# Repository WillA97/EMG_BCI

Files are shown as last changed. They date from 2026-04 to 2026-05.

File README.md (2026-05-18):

# EMG_BCI

## Introduction
This repository contains the documentation, hardware files, and software files for a simple electromyogram front end. The purpose is to create a simple interface to aquire the signals and also improve my hardware and software design skills. It's mostly for fun

## High level requirements

- Amplifier the signals from a 2 electrode from an EMG signal
- transfer the data from to a secondary device

## Hardware block diagram

```mermaid
graph TD
    A[EMG Electrodes<br>500 µV - 1 mV] --> B[Instrumentation Amplifier<br>Gain: 50<br>High Z, High CMRR]
    B --> C[High-Pass Filter<br>Cutoff: 10 Hz]
    C --> D[Gain Stage<br>Gain: 20<br>Total Gain: 1000]
    D --> E[Low-Pass Filter<br>Cutoff: 500 Hz]
    E --> F[Rectifier]
    E --> G[Offset Stage<br>Shift to 1.5V]
    G --> H[ADC 1<br>Un-rectified]
    F --> I[ADC 2<br>Rectified]

```
- The EMG signals will be around 500 uV - 1 mV. Will scale the signals with a gain of about 1000 to make the output swing around 0.5 - 1 V
- The first stage is the instrumentation amplifier. It has a very high impedence input, and large common mode rejection. It also has a gain stage built in, which is chosen as 50
- The second stage would be the high pass filter. Removed any high frequency signals and prevents aliasing when sampling occurs. The cutoff frequency is 10 Hz, which is the lower frequency of the muscle fibers
- The third stage is a gain stage. The gain is set to 20, putting the final gain at 1000.
- The fourth state is the low pass filter. The cutoff frequency was set to 500 Hz, which is the upper limit of the muscle fibers.
- The fifth stage is the rectifier stage.
- The sixth stage is the offset stage, which adds an offset to shift the 0 point of the signal to be 1.5V. This is because many microcontrollers use +3.3V and we want to avoid applying a negative voltage on the ADC
- The sevent stage is the ADC, which can record the EMG signals. To give some options about which signal can be used in the signal processing. I want to use one ADC for the un-rectified signal, and another for the rectified signal.

- There are a couple of options when using the signal for an EMG:
  
  - one option is to use the raw EMG data and do the signal processing on those values. After performing an FFT will get the frequency data from them
  - another option is to rectify the signal, this would give an positive average value for the signal
  - with the rectified signal, can take the RMS and filterd values of it to get the average value of the amount of exertion from the muscles
 
## Communication interface

- The communication interface will be used to transfer the digitized EMG signals to an external device. The ADC chosen (MCP 3202) uses an SPI interface.

## Test results 
Here are some of the results from testing the front end. The analog discovery module was used to insert a signal at the front of the instrumentation amplifier and the output at the different test points was recorded

### Instrumentation amplifier
The following table shows in the input and outputs for the instrumentation amplifier stage:

| Input | Offset | Output PK1 | Output PK2 | Out Offset | Diff | Gain | Offset Gain |
| :--- | :--- | :--- | :--- | :--- | :--- | :--- | :--- |
| 0.01 | 0.5 | 1.478 | 1.5204 | 1.4992 | 0.0424 | 4.24 | 1.8984 |
| 0.05 | 0.5 | 1.398 | 1.598 | 1.498 | 0.2 | 4 | 1.896 |
| 0.06 | 0.5 | 1.381 | 1.6175 | 1.49925 | 0.2365 | 3.94166667 | 1.8985 |
| 0.1 | 0.5 | 1.3 | 1.695 | 1.4975 | 0.395 | 3.95 | 1.895 |
| 0.15 | 0.5 | 1.202 | 1.796 | 1.499 | 0.594 | 3.96 | 1.898 |
| 0.05 | 0.1 | 0.621 | 0.819 | 0.72 | 0.198 | 3.96 | 1.7 |
| 0.05 | 0.2 | 0.814 | 1.01 | 0.912 | 0.196 | 3.92 | 1.81 |
| 0.05 | 0.4 | 1.207 | 1.402 | 1.3045 | 0.195 | 3.9 | 1.88625 |
| 0.05 | 0.6 | 1.596 | 1.792 | 1.694 | 0.196 | 3.92 | 1.90666667 |
| 0.05 | 0.7 | 1.789 | 1.985 | 1.887 | 0.196 | 3.92 | 1.91 |
| 0.05 | 0.8 | 1.984 | 2.181 | 2.0825 | 0.197 | 3.94 | 1.915625 |
| 0.05 | 0.9 | 2.181 | 2.376 | 2.2785 | 0.195 | 3.9 | 1.92055556 |
| 0.05 | 0 | 0.547 | 0.626 | 0.5865 | 0.079 | 1.58 | *Undefined (NaN)* |

couple of things to note:
- for some reason the gain of the amplifier is 4. From the datasheet since the gain pins is connected to HIGH it should be 50. Not sure why it isn't working as it should. Will have to do more investigation
- the offset did not work as I expected. It just cut off the zero point of the amplifier so when a negative value was put in, it was still cut off. I should have connected a negative supply to it in order to not lose the negative information or apply an offset to it using a summing amplifer. Since there is a high pass filter after it, the offset would likely removed anyways.

### TP2 - Output of the high pass filter and gain stage

The following table shows the data:

| Input | offset | output pk1 | output pk2 | out offset | diff | gain |
| :--- | :--- | :--- | :--- | :--- | :--- | :--- |
| 0.01 | 0.5 | -0.406 | 0.388 | -0.018 | 0.794 | 79.4 |
| 0.001 | 0.5 | -0.0375 | 0.0429 | 0.0054 | 0.0804 | 80.4 |
| 0.015 | 0.5 | -0.59 | 0.602 | 0.012 | 1.192 | 79.46667 |
| 0.02 | 0.5 | -0.782 | 0.798 | 0.016 | 1.58 | 79 |
| 0.03 | 0.5 | -1.118 | 1.1959 | 0.0159 | 2.3759 | 79.19667 |

### TP3 - Output of the low pass filter / The entire system

| Input | offset | output pk1 | output pk2 | out offset | diff | gain |
| :--- | :--- | :--- | :--- | :--- | :--- | :--- |
| 0.03 | 0.5 | -1.00E-02 | 5.64E-03 | -2.20E-03 | 1.57E-02 | 0.522333 |
| 0.03 | 0.5 | -6.79E-01 | 6.79E-01 | 0.00E+00 | 1.36E+00 | 45.26667 |
| 0.03 | 0.5 | -1.178 | 1.178 | 0.00E+00 | 2.36E+00 | 78.53333 |
| 0.03 | 0.5 | -1.178 | 1.178 | 0.00E+00 | 2.36E+00 | 78.53333 |
| 0.03 | 0.5 | -1.178 | 1.178 | 0.00E+00 | 2.36E+00 | 78.53333 |
| 0.03 | 0.5 | -1.1315 | 1.131 | -2.50E-04 | 2.26E+00 | 75.41667 |
| 0.03 | 0.5 | -1.014 | 1.014 | 0.00E+00 | 2.03E+00 | 67.6 |
| 0.03 | 0.5 | -8.62E-01 | 8.68E-01 | 3.00E-03 | 1.73E+00 | 57.66667 |
| 0.03 | 0.5 | -7.10E-01 | 7.04E-01 | -3.00E-03 | 1.41E+00 | 47.13333 |
| 0.03 | 0.5 | -5.64E-01 | 5.70E-01 | 3.00E-03 | 1.13E+00 | 37.8 |
| 0.03 | 0.5 | -4.70E-01 | 4.59E-01 | -5.50E-03 | 9.29E-01 | 30.96667 |
| 0.03 | 0.5 | -3.65E-01 | 3.71E-01 | 3.00E-03 | 7.36E-01 | 24.53333 |
| 0.03 | 0.5 | -3.12E-01 | 3.12E-01 | 0.00E+00 | 6.24E-01 | 20.8 |
| 0.03 | 0.5 | -2.01E-01 | 2.01E-01 | 0.00E+00 | 4.02E-01 | 13.4 |
| 0.03 | 0.5 | -1.45E-01 | 1.42E-01 | -1.50E-03 | 2.87E-01 | 9.566667 |
| 0.03 | 0

The graphs of the final table are:



The frequency response has the desired shape. The cutoff frequnecy is around 500 Hz. However, since the gain stage of the instrumentation amplifier was off for some reason, the final gain is off as well. This is annoying.

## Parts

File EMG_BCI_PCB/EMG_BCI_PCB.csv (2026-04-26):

Id | Designator | Footprint | Quantity | Designation | Supplier and ref
1 | U3,U2 | TSSOP-14_4.4x5mm_P0.65mm | 2 | ADA4807-4ARUZ
2 | C4,C25,C1,C3,C27 | C_0603_1608Metric_Pad1.08x0.95mm_HandSolder | 5 | 1uF
3 | R16,R13,R15,R14 | R_0603_1608Metric_Pad0.98x0.95mm_HandSolder | 4 | 1K
4 | C15,C16,C22,C21,C8,C24 | C_0603_1608Metric_Pad1.08x0.95mm_HandSolder | 6 | 0.1uF
5 | C26,C29,C30,C18 | C_0603_1608Metric_Pad1.08x0.95mm_HandSolder | 4 | 2.2uF
6 | D4,D3 | D_SOD-523 | 2 | 1N4148WT
7 | TP6,TP3,TP1,TP2,TP10,TP9,TP4,TP5,TP7,TP11,TP8 | PinHeader_1x01_P2.54mm_Vertical | 11 | TestPoint
8 | R21 | R_0603_1608Metric_Pad0.98x0.95mm_HandSolder | 1 | 10K
9 | U1 | SOT-23-THIN | 1 | INA350CDS
10 | R11 | R_0603_1608Metric_Pad0.98x0.95mm_HandSolder | 1 | 11k
11 | C32,C37,C36 | C_0603_1608Metric_Pad1.08x0.95mm_HandSolder | 3 | 33u
12 | R4,R7,R5,R12,R2,R6 | R_0603_1608Metric_Pad0.98x0.95mm_HandSolder | 6 | 10k
13 | R17 | R_0603_1608Metric_Pad0.98x0.95mm_HandSolder | 1 | 72.5K
14 | C10,C9 | C_0603_1608Metric_Pad1.08x0.95mm_HandSolder | 2 | 1u
15 | J2 | PinSocket_1x02_P2.54mm_Vertical | 1 | 2.54 mm header
16 | J1 | PinSocket_1x08_P2.54mm_Vertical_SMD_Pin1Right | 1 | Conn_01x08_Pin
17 | C2 | C_0603_1608Metric_Pad1.08x0.95mm_HandSolder | 1 | 1 nF
18 | R1 | R_0603_1608Metric_Pad0.98x0.95mm_HandSolder | 1 | 190k
19 | C11 | C_0603_1608Metric_Pad1.08x0.95mm_HandSolder | 1 | 0.0047u
20 | R3 | R_0603_1608Metric_Pad0.98x0.95mm_HandSolder | 1 | 2k
21 | C23,C7,C6,C13,C20,C5,C19,C14 | C_0603_1608Metric_Pad1.08x0.95mm_HandSolder | 8 | 4.7uF
22 | R9 | R_0603_1608Metric_Pad0.98x0.95mm_HandSolder | 1 | 36k
23 | R24,R25 | R_0603_1608Metric_Pad0.98x0.95mm_HandSolder | 2 | 200
24 | U7 | SOT-23-6 | 1 | LM2776
25 | U8 | SOT-23-6 | 1 | MCP1501-18xCH
26 | C17 | C_0603_1608Metric_Pad1.08x0.95mm_HandSolder | 1 | 47pF
27 | RV1 | Potentiometer_Piher_PT-10-V10_Vertical | 1 | R_Potentiometer
28 | R8 | R_0603_1608Metric_Pad0.98x0.95mm_HandSolder | 1 | 56k
29 | U9 | 8-MSOP | 1 | MCP3202
30 | U5 | SOIC-8_3.9x4.9mm_P1.27mm | 1 | MCP1727-3302xSN
31 | R10 | R_0603_1608Metric_Pad0.98x0.95mm_HandSolder | 1 | 22k
32 | C12 | C_0603_1608Metric_Pad1.08x0.95mm_HandSolder | 1 | 0.01u

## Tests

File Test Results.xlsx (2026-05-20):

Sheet: Instrumentation_Amplifier
Input | offset | output pk1 | output pk2 | out offset | diff | gain | offset gain | freq | 750 Hz
0.01 | 0.5 | 1.478 | 1.5204 | 1.4992 | 0.0424 | 4.24 | 1.8984 |  | 751 Hz
0.05 | 0.5 | 1.398 | 1.598 | 1.498 | 0.2 | 4 | 1.896 |  | 752 Hz
0.06 | 0.5 | 1.381 | 1.6175 | 1.49925 | 0.2365 | 3.941666667 | 1.8985 |  | 753 Hz
0.1 | 0.5 | 1.3 | 1.695 | 1.4975 | 0.395 | 3.95 | 1.895 |  | 754 Hz
0.15 | 0.5 | 1.202 | 1.796 | 1.499 | 0.594 | 3.96 | 1.898 |  | 755 Hz
0.05 | 0.1 | 0.621 | 0.819 | 0.72 | 0.198 | 3.96 | 1.7 |  | 756 Hz
0.05 | 0.2 | 0.814 | 1.01 | 0.912 | 0.196 | 3.92 | 1.81 |  | 757 Hz
0.05 | 0.4 | 1.207 | 1.402 | 1.3045 | 0.195 | 3.9 | 1.88625
0.05 | 0.6 | 1.596 | 1.792 | 1.694 | 0.196 | 3.92 | 1.906666667
0.05 | 0.7 | 1.789 | 1.985 | 1.887 | 0.196 | 3.92 | 1.91
0.05 | 0.8 | 1.984 | 2.181 | 2.0825 | 0.197 | 3.94 | 1.915625
0.05 | 0.9 | 2.181 | 2.376 | 2.2785 | 0.195 | 3.9 | 1.920555556
0.05 | 0 | 0.547 | 0.626 | 0.5865 | 0.079 | 1.58 | #DIV/0!
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

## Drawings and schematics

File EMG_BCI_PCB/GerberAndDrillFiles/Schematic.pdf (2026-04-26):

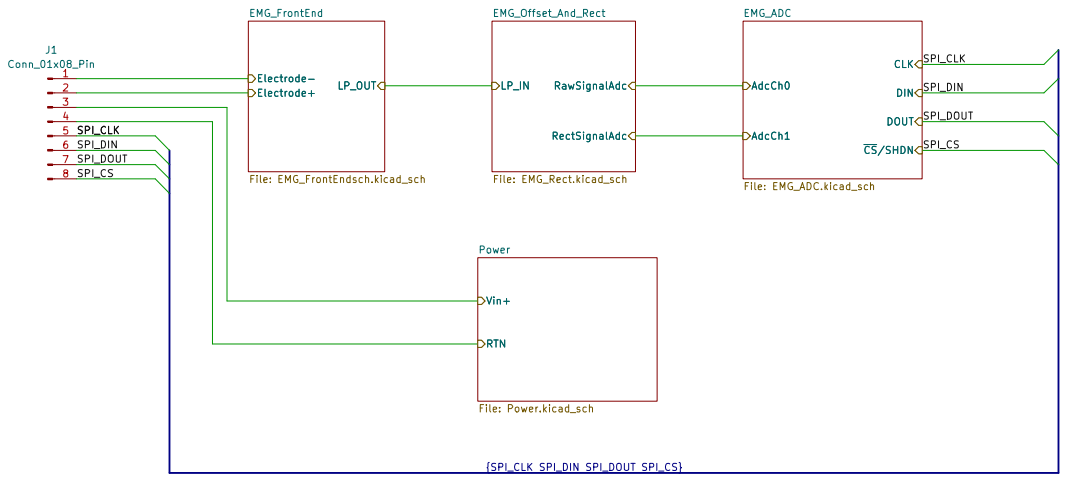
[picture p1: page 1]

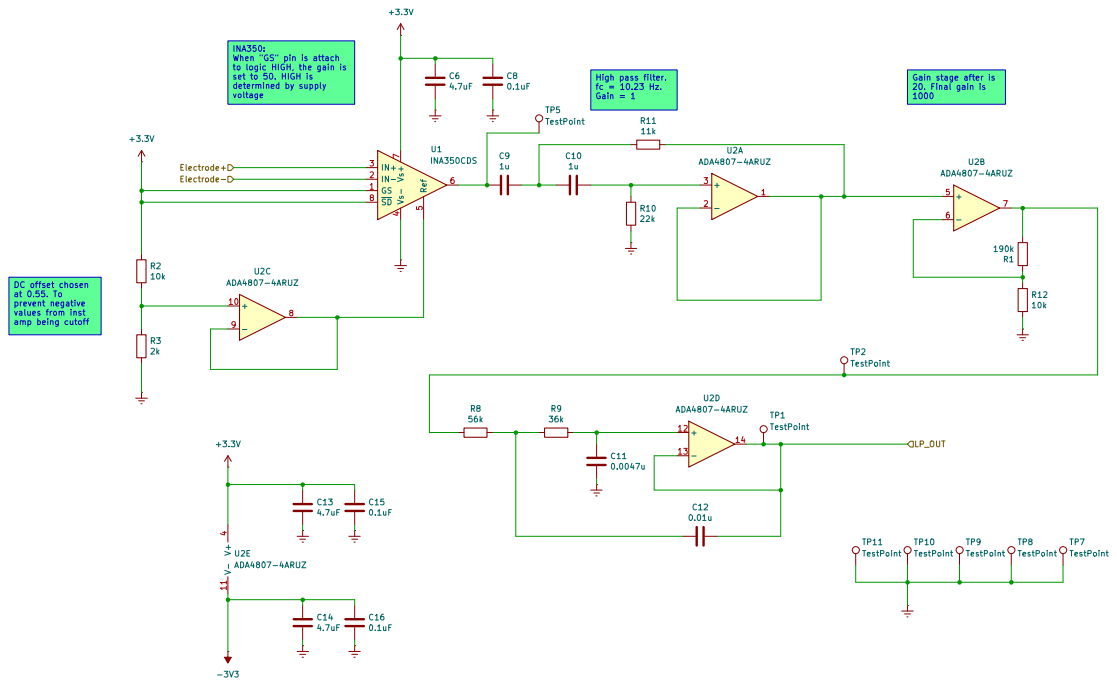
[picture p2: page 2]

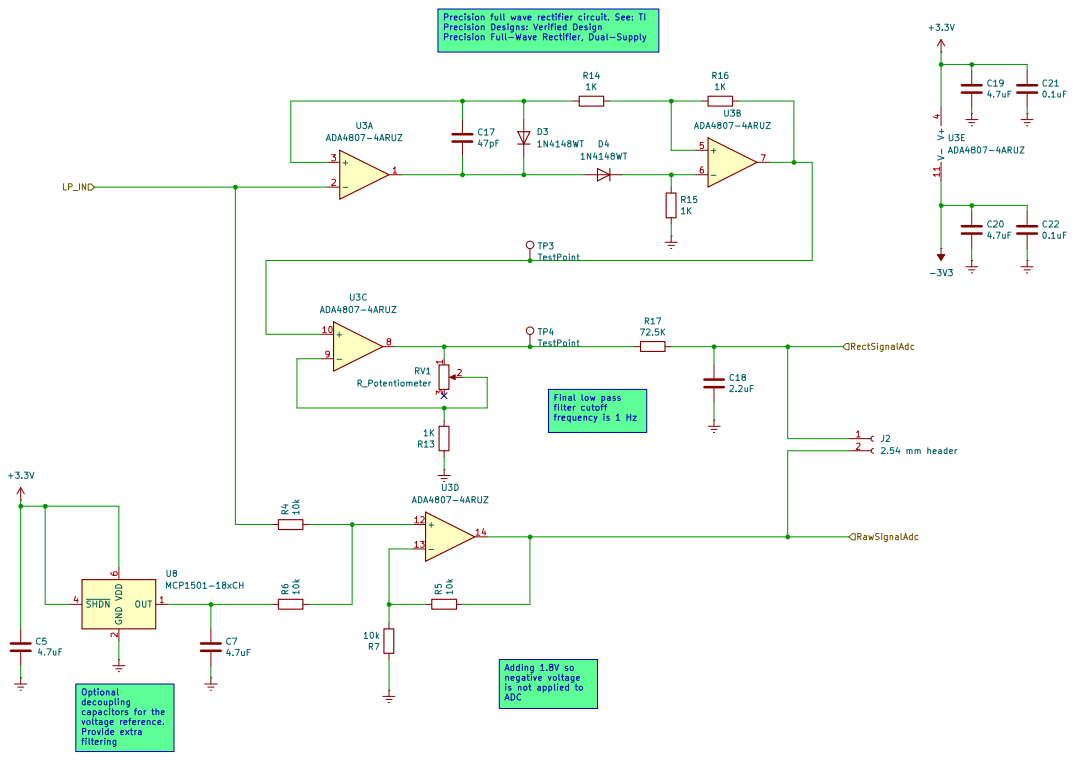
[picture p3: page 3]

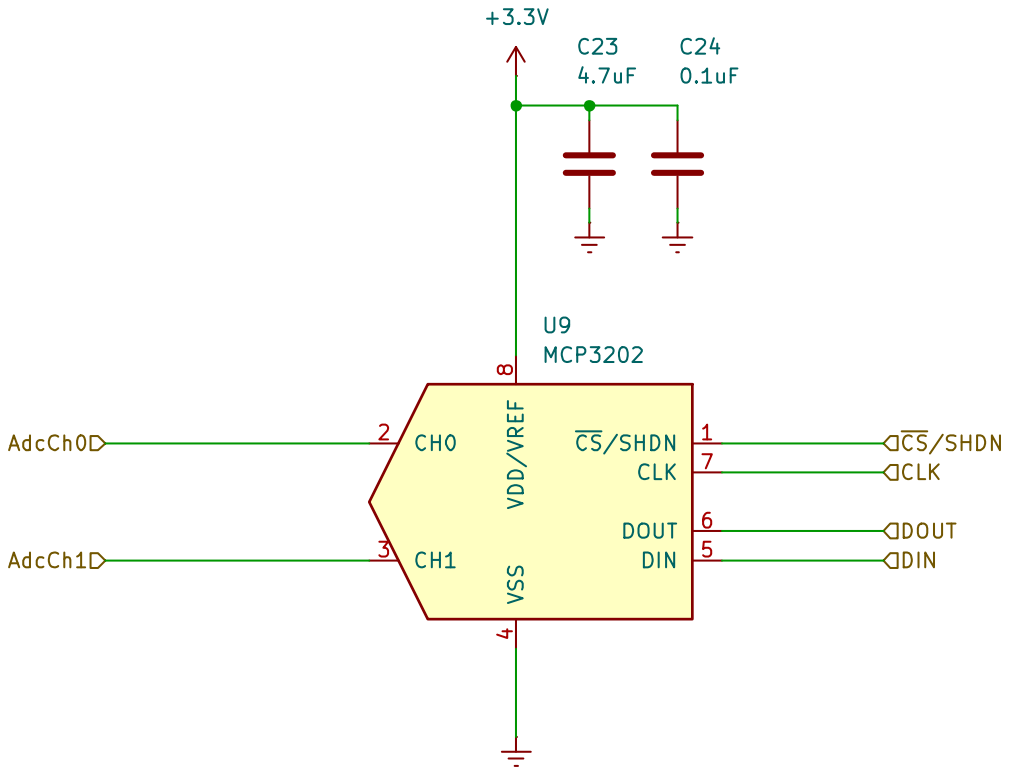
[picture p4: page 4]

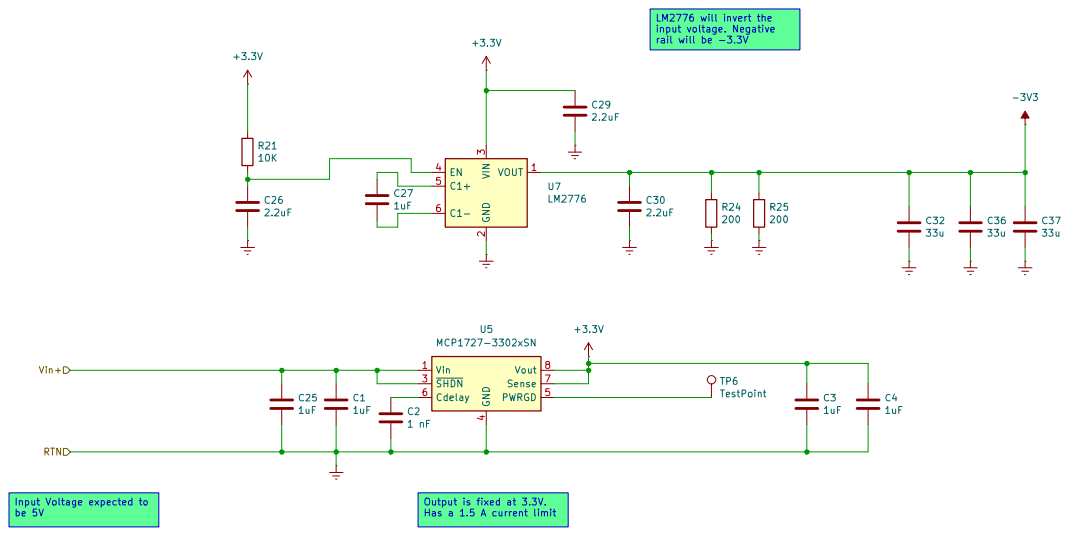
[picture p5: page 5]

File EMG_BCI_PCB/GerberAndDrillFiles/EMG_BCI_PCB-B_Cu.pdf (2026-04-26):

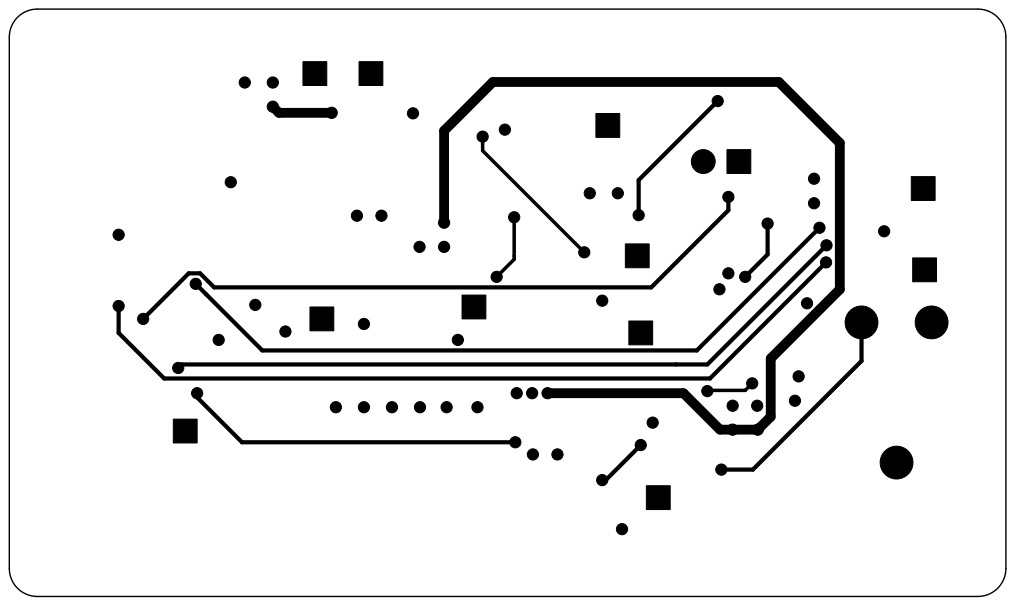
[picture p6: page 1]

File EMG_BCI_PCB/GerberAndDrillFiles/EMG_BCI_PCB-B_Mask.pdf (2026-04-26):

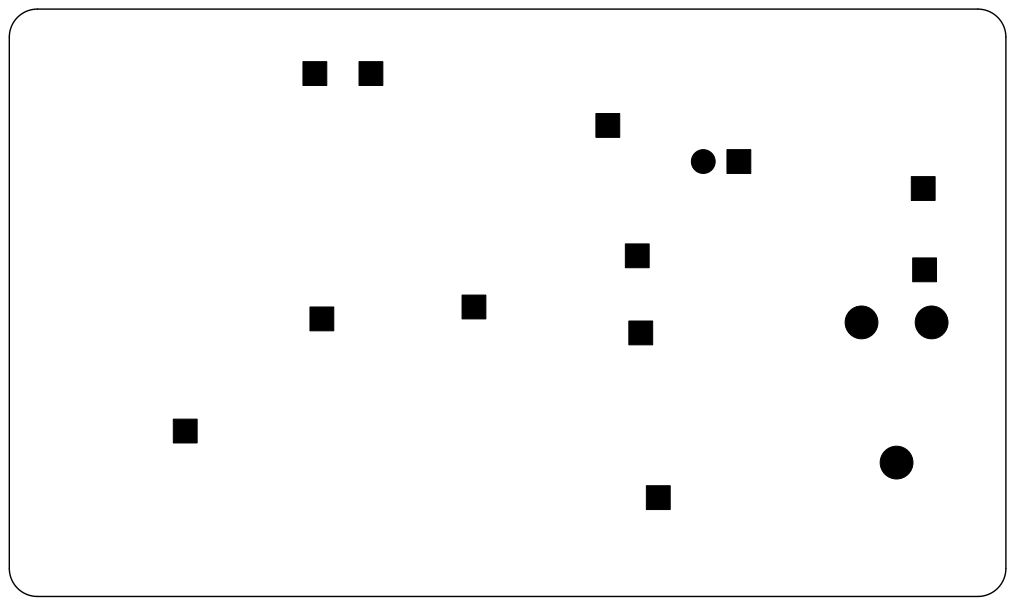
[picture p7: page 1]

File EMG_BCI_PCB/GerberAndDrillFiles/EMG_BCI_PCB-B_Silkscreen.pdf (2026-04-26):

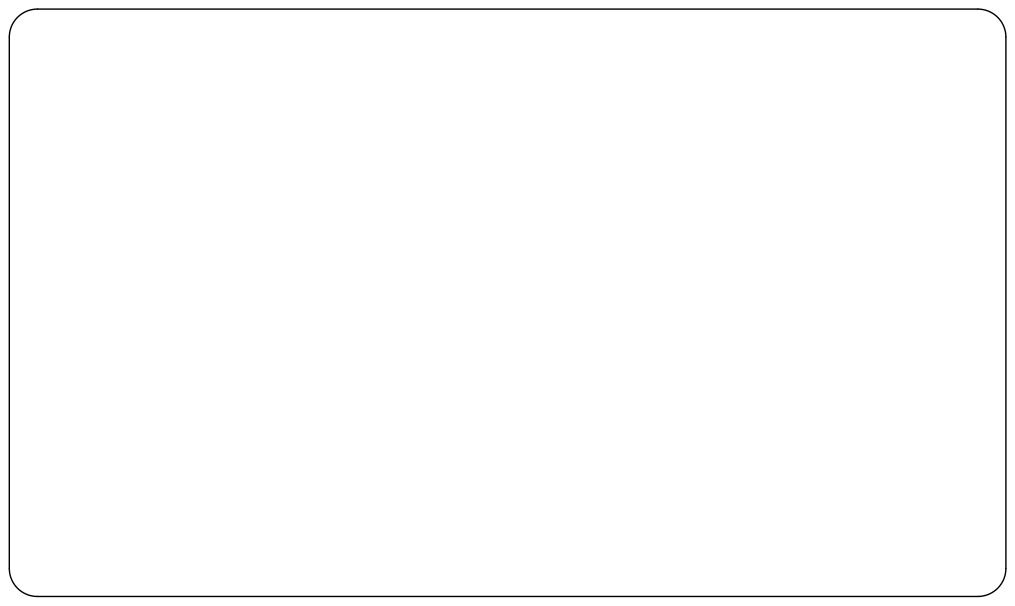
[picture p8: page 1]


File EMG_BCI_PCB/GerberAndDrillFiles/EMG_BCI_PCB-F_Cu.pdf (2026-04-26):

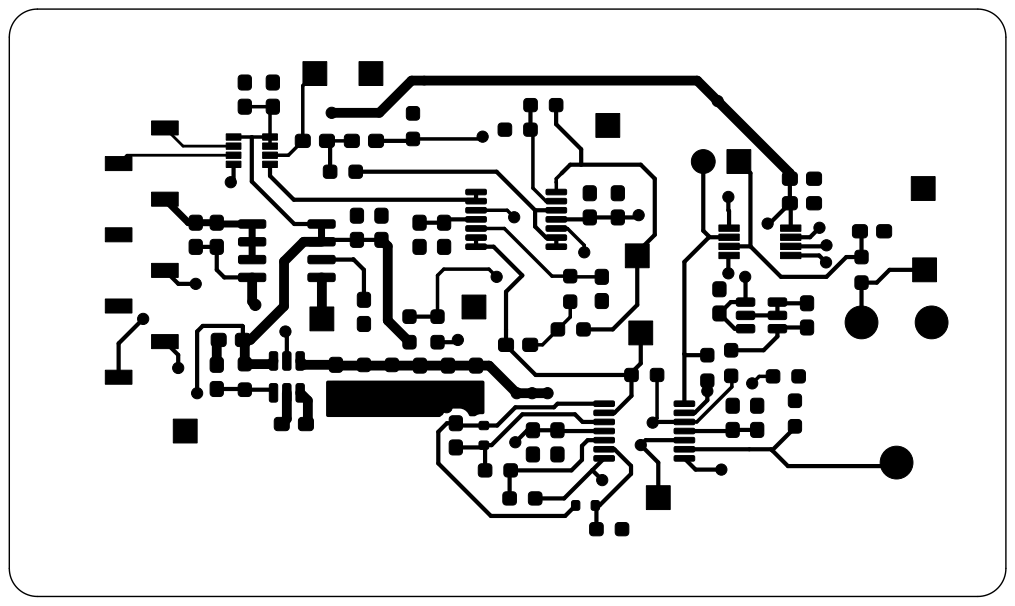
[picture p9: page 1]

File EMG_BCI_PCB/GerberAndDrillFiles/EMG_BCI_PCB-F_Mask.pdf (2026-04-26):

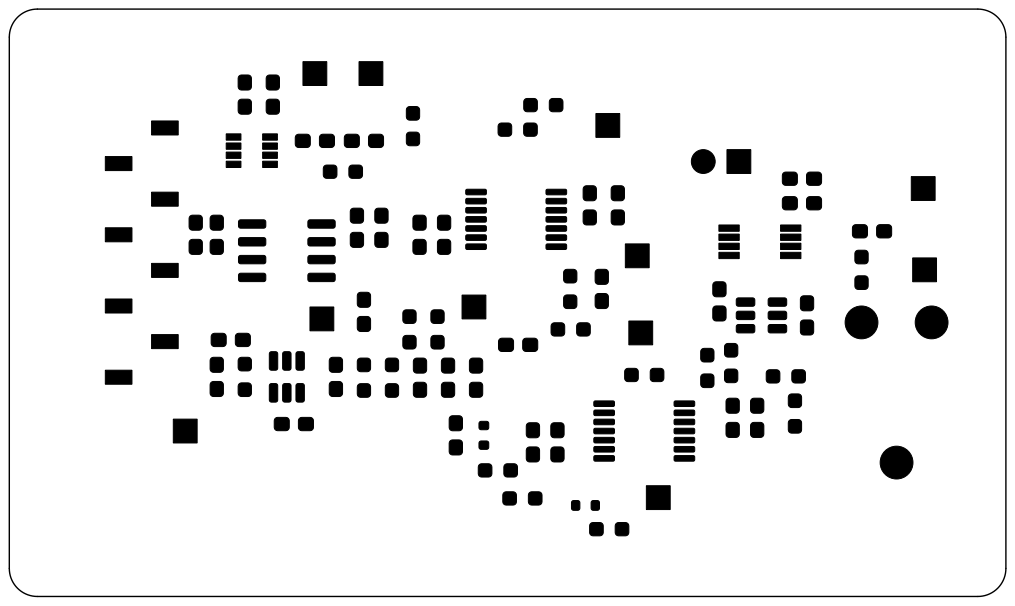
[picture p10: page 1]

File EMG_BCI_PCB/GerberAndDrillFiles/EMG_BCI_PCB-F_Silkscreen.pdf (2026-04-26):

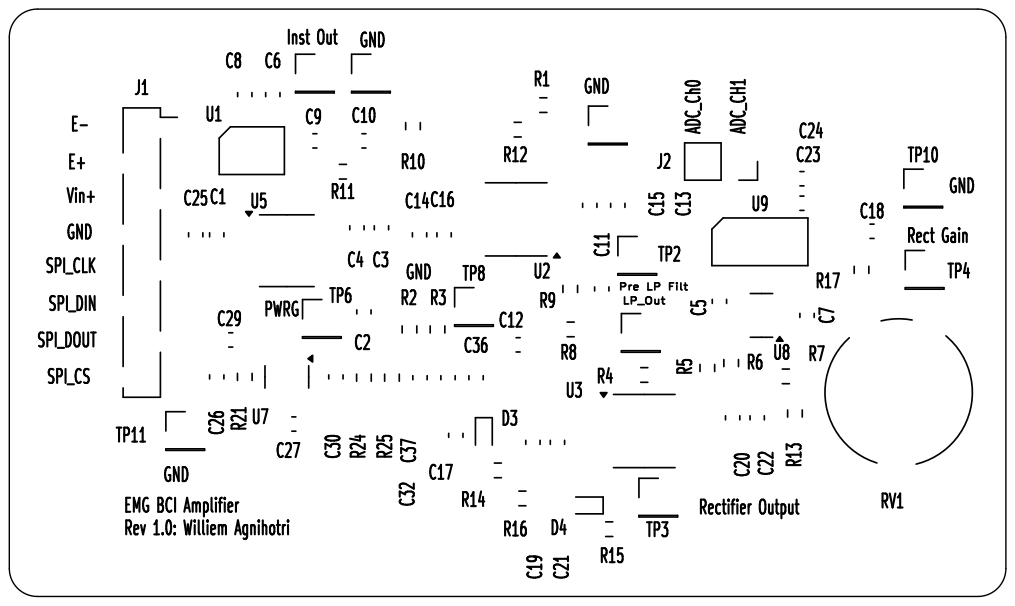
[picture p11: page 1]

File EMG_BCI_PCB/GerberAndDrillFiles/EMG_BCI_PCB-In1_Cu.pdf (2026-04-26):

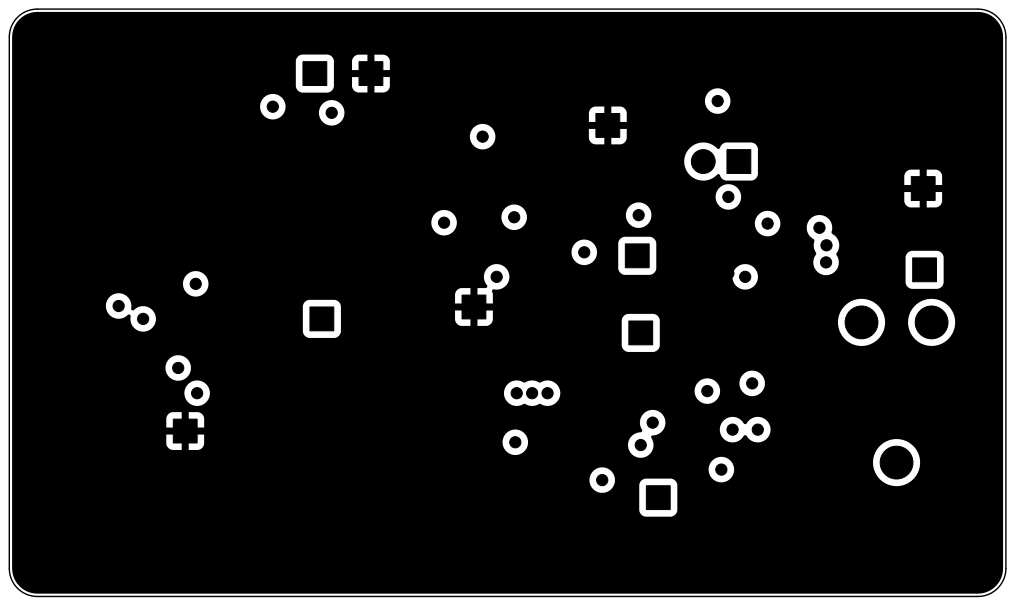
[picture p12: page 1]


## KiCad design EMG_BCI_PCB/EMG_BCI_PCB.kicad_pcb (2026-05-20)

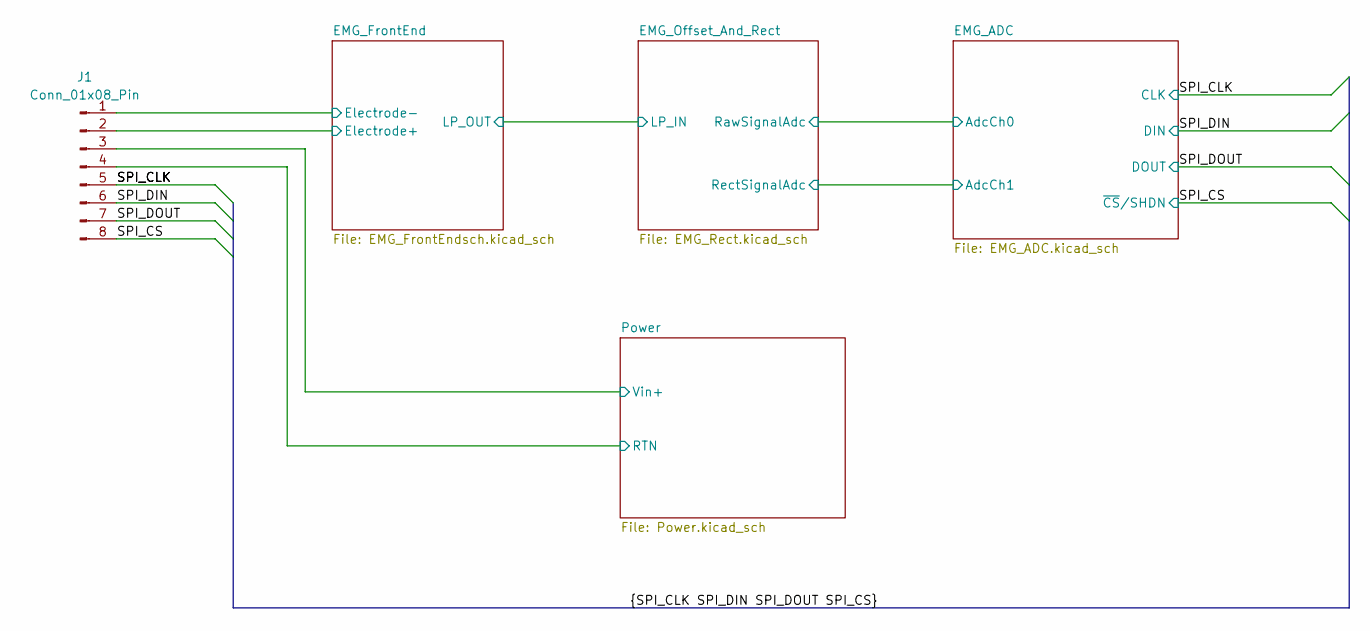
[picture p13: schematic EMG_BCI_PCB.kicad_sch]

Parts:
J1: Conn_01x08_Pin; PinSocket_1x08_P2.54mm_Vertical_SMD_Pin1Right

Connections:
/EMG_FrontEnd/Electrode+: J1.2; also elsewhere on the board
/EMG_FrontEnd/Electrode-: J1.1; also elsewhere on the board
/Power/Vin+: J1.3; also elsewhere on the board
/SPI_CLK: J1.5; also elsewhere on the board
/SPI_CS: J1.8; also elsewhere on the board
/SPI_DIN: J1.6; also elsewhere on the board
/SPI_DOUT: J1.7; also elsewhere on the board
Earth: J1.4; also elsewhere on the board

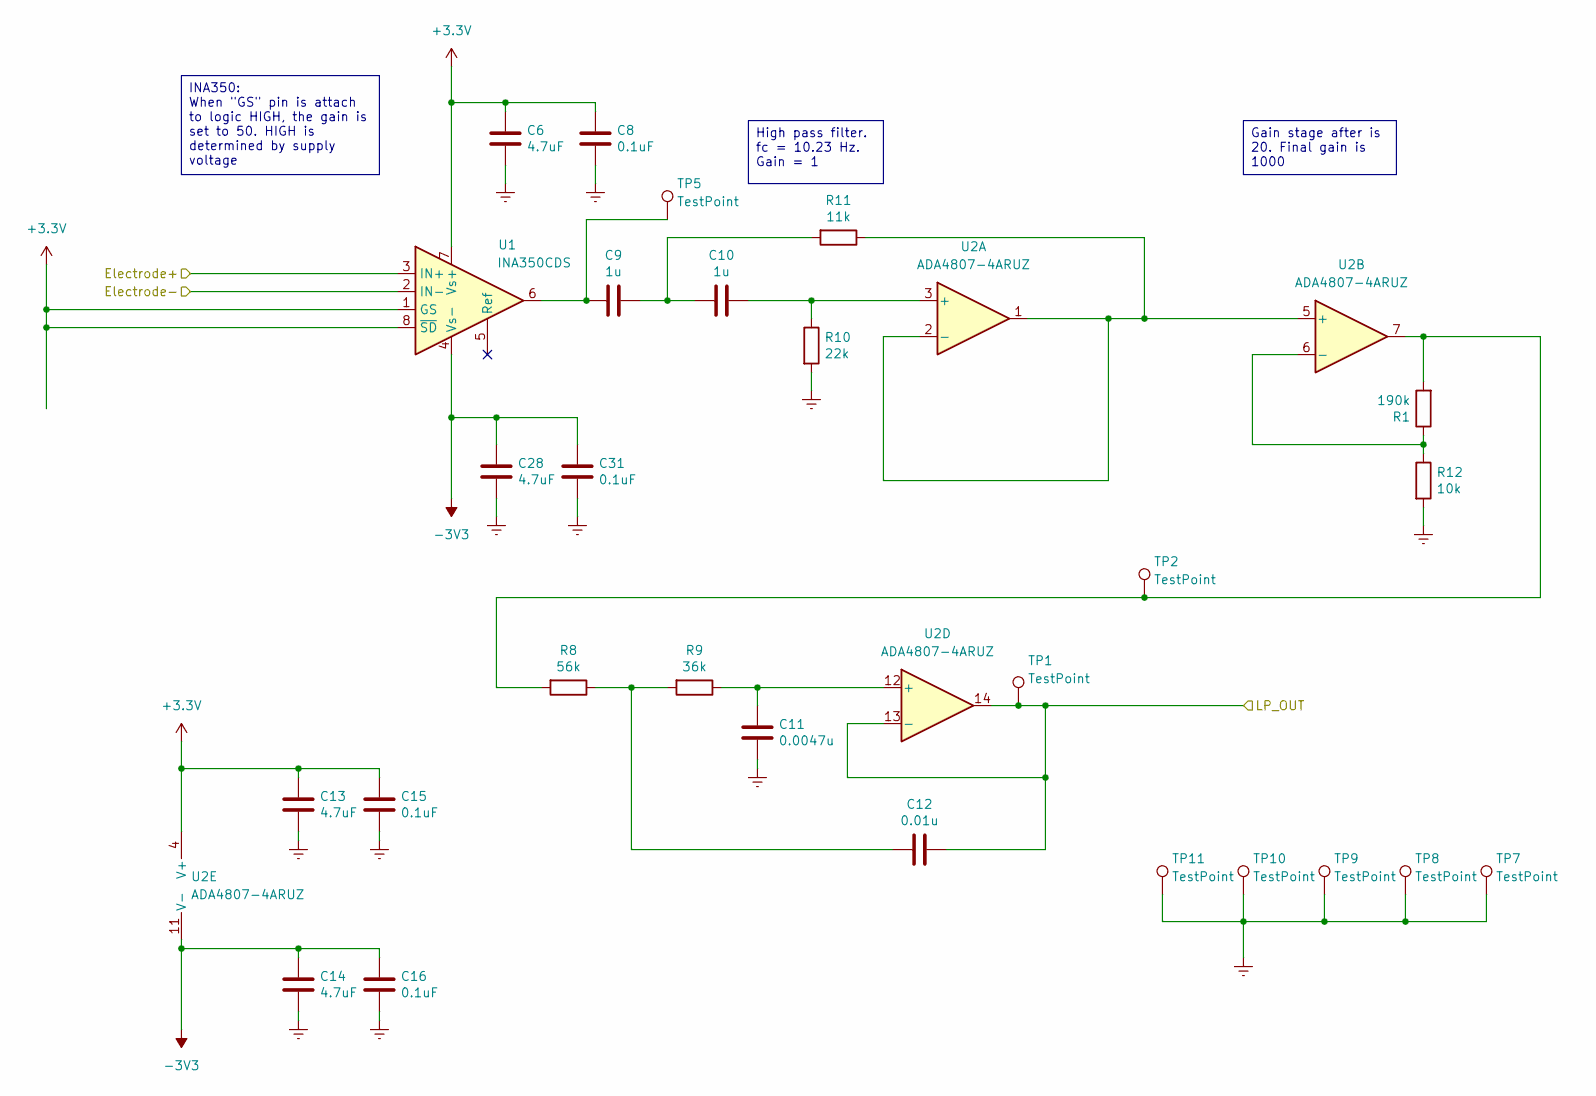
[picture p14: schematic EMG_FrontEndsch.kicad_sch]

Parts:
C6, C13, C14, C28: 4.7uF; C_0603_1608Metric_Pad1.08x0.95mm_HandSolder
C8, C15, C16, C31: 0.1uF; C_0603_1608Metric_Pad1.08x0.95mm_HandSolder
C9, C10: 1u; C_0603_1608Metric_Pad1.08x0.95mm_HandSolder
C11: 0.0047u; C_0603_1608Metric_Pad1.08x0.95mm_HandSolder
C12: 0.01u; C_0603_1608Metric_Pad1.08x0.95mm_HandSolder
R1: 190k; R_0603_1608Metric_Pad0.98x0.95mm_HandSolder
R8: 56k; R_0603_1608Metric_Pad0.98x0.95mm_HandSolder
R9: 36k; R_0603_1608Metric_Pad0.98x0.95mm_HandSolder
R10: 22k; R_0603_1608Metric_Pad0.98x0.95mm_HandSolder
R11: 11k; R_0603_1608Metric_Pad0.98x0.95mm_HandSolder
R12: 10k; R_0603_1608Metric_Pad0.98x0.95mm_HandSolder
TP1, TP2, TP5, TP7, TP8, TP9, TP10, TP11: TestPoint; PinHeader_1x01_P2.54mm_Vertical
U1: INA350CDS; SOT-23-THIN
U2: ADA4807-4ARUZ; TSSOP-14_4.4x5mm_P0.65mm

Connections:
+3.3V: C6.2, C8.2, C13.2, C15.2, U1.1 (GS), U1.7 (Vs+), U1.8 (~SD), U2.4 (V+); also elsewhere on the board
-3V3: C14.2, C16.2, C28.1, C31.1, U1.4 (Vs-), U2.11 (V-); also elsewhere on the board
/EMG_FrontEnd/Electrode+: U1.3 (IN+); also elsewhere on the board
/EMG_FrontEnd/Electrode-: U1.2 (IN-); also elsewhere on the board
/EMG_FrontEnd/LP_OUT: C12.2, TP1.1 (1_1), U2.13 (-), U2.14; also elsewhere on the board
Earth: C6.1, C8.1, C11.1, C13.1, C14.1, C15.1, C16.1, C28.2, C31.2, R10.2, R12.2, TP7.1 (1_1), TP8.1 (1_1), TP9.1 (1_1), TP10.1 (1_1), TP11.1 (1_1); also elsewhere on the board
unnamed: C9.2, TP5.1 (1_1), U1.6
unnamed: C9.1, C10.2, R11.2
unnamed: C12.1, R8.1, R9.2
unnamed: R1.2, R8.2, TP2.1 (1_1), U2.7
unnamed: C10.1, R10.1, U2.3 (+)
unnamed: R11.1, U2.1, U2.2 (-), U2.5 (+)
unnamed: R1.1, R12.1, U2.6 (-)
unnamed: C11.2, R9.1, U2.12 (+)

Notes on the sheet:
INA350: When "GS" pin is attach to logic HIGH, the gain is set to 50. HIGH is determined by supply voltage
High pass filter. fc = 10.23 Hz. Gain = 1
Gain stage after is 20. Final gain is 1000

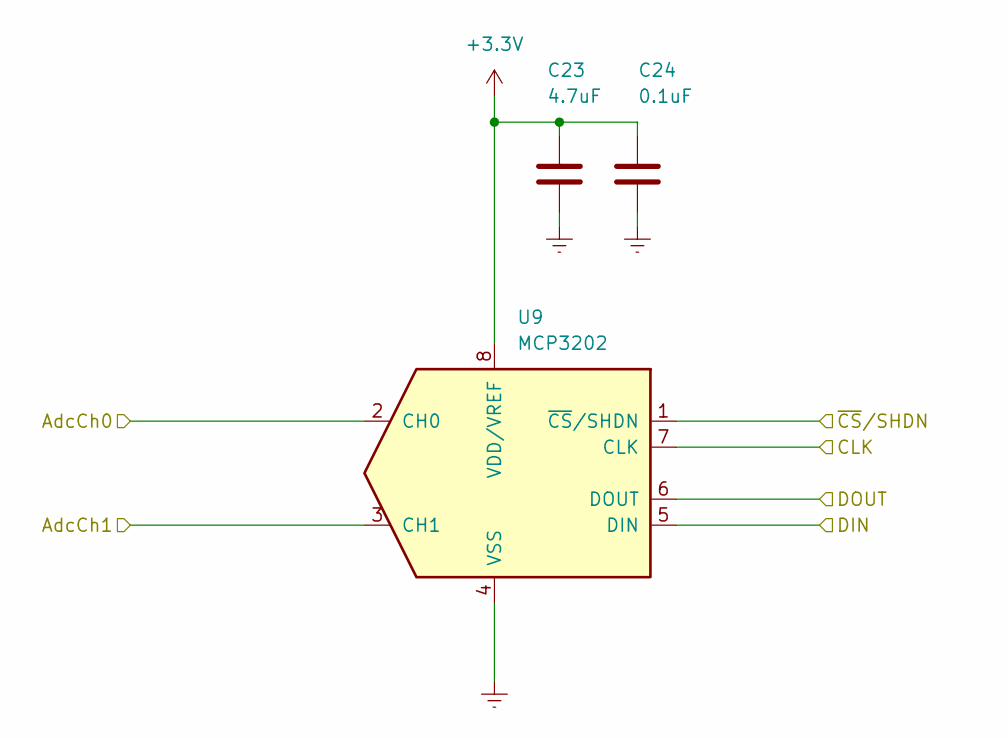
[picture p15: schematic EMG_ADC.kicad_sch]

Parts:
C23: 4.7uF; C_0603_1608Metric_Pad1.08x0.95mm_HandSolder
C24: 0.1uF; C_0603_1608Metric_Pad1.08x0.95mm_HandSolder
U9: MCP3202; 8-MSOP

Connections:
+3.3V: C23.1, C24.1, U9.8 (VDD/VREF); also elsewhere on the board
/EMG_ADC/AdcCh0: U9.2 (CH0); also elsewhere on the board
/EMG_ADC/AdcCh1: U9.3 (CH1); also elsewhere on the board
/SPI_CLK: U9.7 (CLK); also elsewhere on the board
/SPI_CS: U9.1 (~CS/SHDN); also elsewhere on the board
/SPI_DIN: U9.5 (DIN); also elsewhere on the board
/SPI_DOUT: U9.6 (DOUT); also elsewhere on the board
Earth: C23.2, C24.2, U9.4 (VSS); also elsewhere on the board

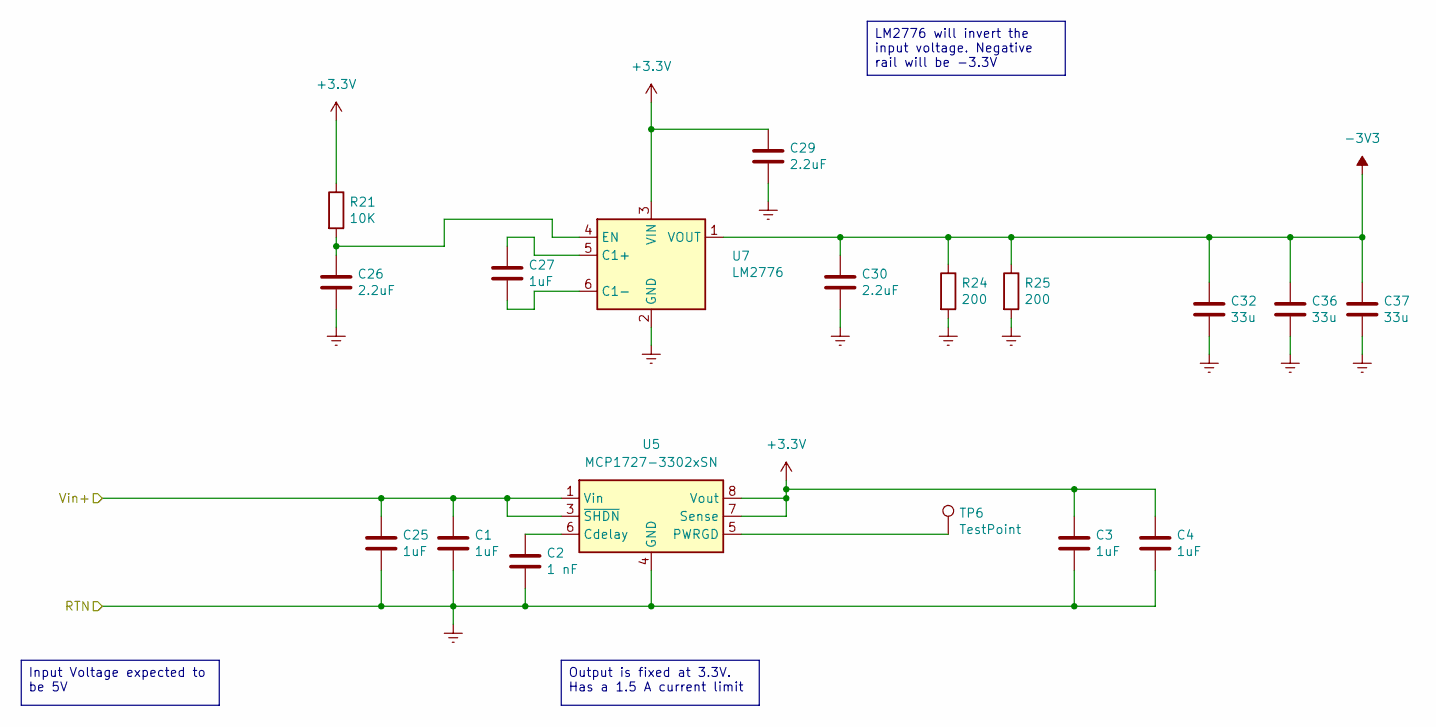
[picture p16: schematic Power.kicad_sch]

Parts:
C1, C3, C4, C25, C27: 1uF; C_0603_1608Metric_Pad1.08x0.95mm_HandSolder
C2: 1 nF; C_0603_1608Metric_Pad1.08x0.95mm_HandSolder
C26, C29, C30: 2.2uF; C_0603_1608Metric_Pad1.08x0.95mm_HandSolder
C32, C36, C37: 33u; C_0603_1608Metric_Pad1.08x0.95mm_HandSolder
R21: 10K; R_0603_1608Metric_Pad0.98x0.95mm_HandSolder
R24, R25: 200; R_0603_1608Metric_Pad0.98x0.95mm_HandSolder
TP6: TestPoint; PinHeader_1x01_P2.54mm_Vertical
U5: MCP1727-3302xSN; SOIC-8_3.9x4.9mm_P1.27mm
U7: LM2776; SOT-23-6

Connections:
+3.3V: C3.1, C4.1, C29.1, R21.1, U5.7 (Sense), U5.8 (Vout), U7.3 (VIN); also elsewhere on the board
-3V3: C30.1, C32.1, C36.1, C37.1, R24.1, R25.1, U7.1 (VOUT); also elsewhere on the board
/Power/Vin+: C1.1, C25.1, U5.1 (Vin), U5.2 (Vin), U5.3 (~SHDN); also elsewhere on the board
Earth: C1.2, C2.2, C3.2, C4.2, C25.2, C26.2, C29.2, C30.2, C32.2, C36.2, C37.2, R24.2, R25.2, U5.4 (GND), U7.2 (GND); also elsewhere on the board
unnamed: C2.1, U5.6 (Cdelay)
unnamed: TP6.1 (1_1), U5.5 (PWRGD)
unnamed: C27.1, U7.5 (C1+)
unnamed: C27.2, U7.6 (C1-)
unnamed: C26.1, R21.2, U7.4 (EN)

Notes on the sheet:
Input Voltage expected to be 5V
Output is fixed at 3.3V. Has a 1.5 A current limit
LM2776 will invert the input voltage. Negative rail will be -3.3V

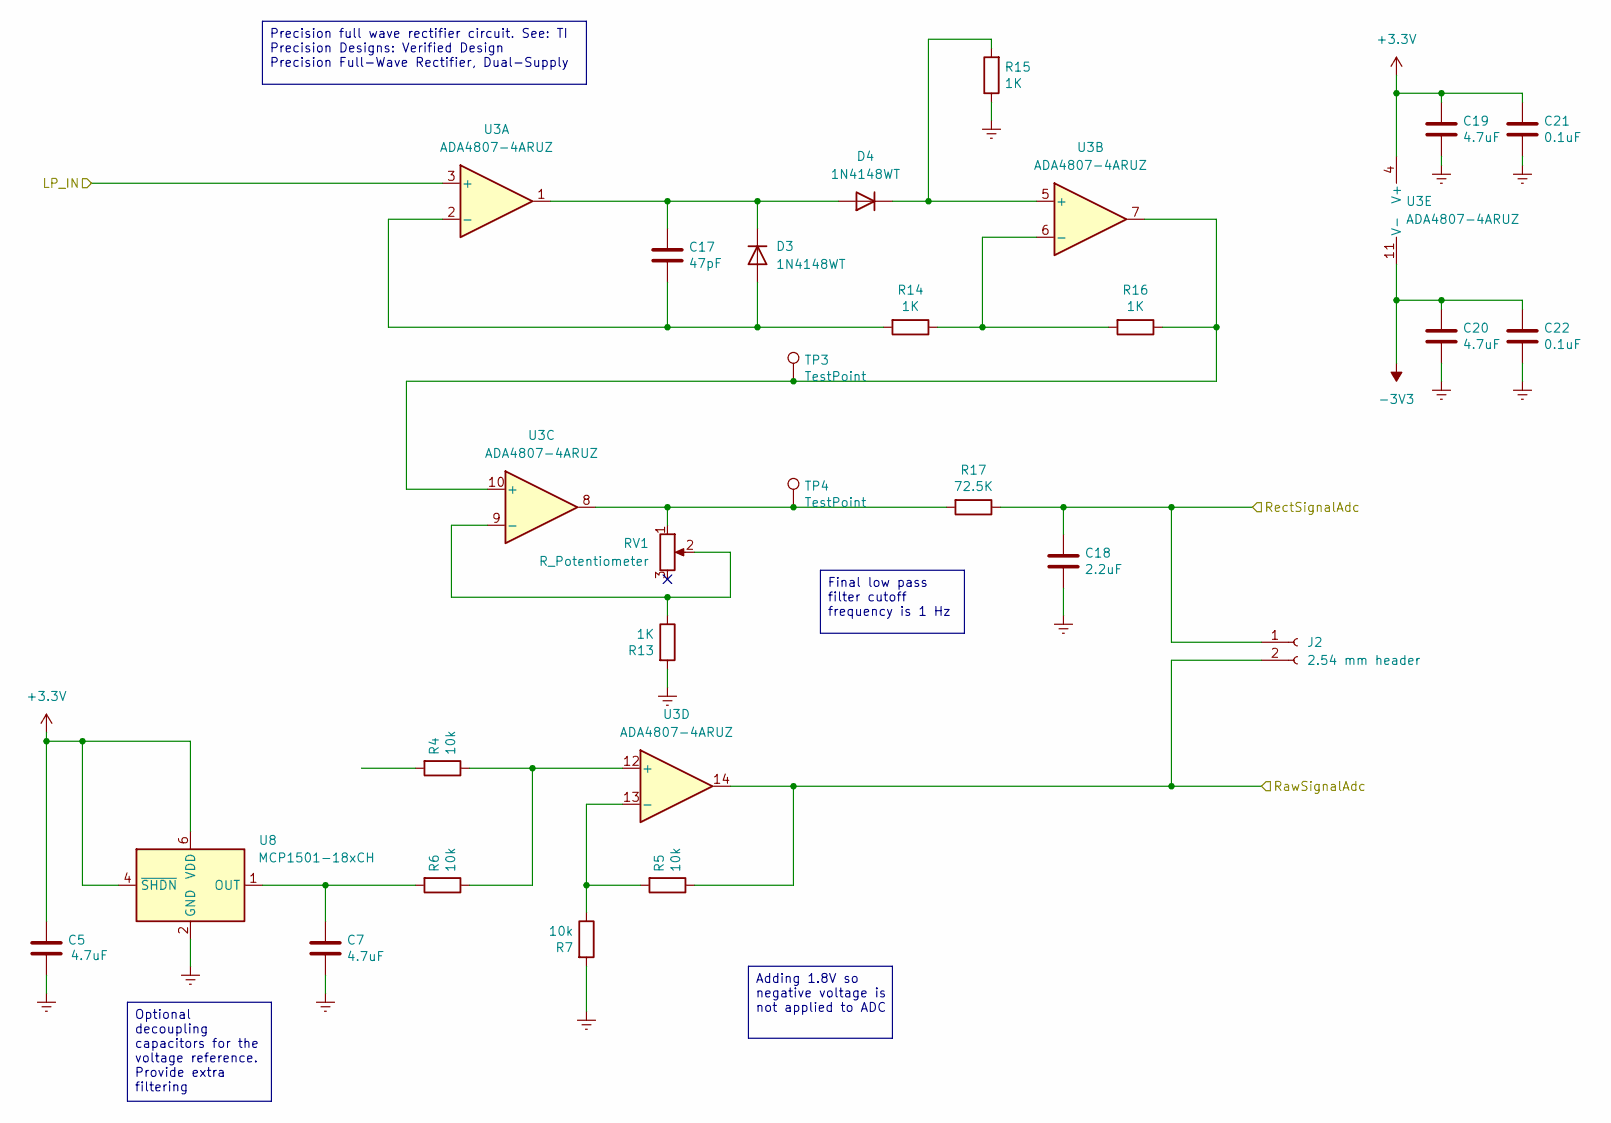
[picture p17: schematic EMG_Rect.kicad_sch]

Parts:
C5, C7, C19, C20: 4.7uF; C_0603_1608Metric_Pad1.08x0.95mm_HandSolder
C17: 47pF; C_0603_1608Metric_Pad1.08x0.95mm_HandSolder
C18: 2.2uF; C_0603_1608Metric_Pad1.08x0.95mm_HandSolder
C21, C22: 0.1uF; C_0603_1608Metric_Pad1.08x0.95mm_HandSolder
D3, D4: 1N4148WT; D_SOD-523
J2: 2.54 mm header; PinSocket_1x02_P2.54mm_Vertical
R4, R5, R6, R7: 10k; R_0603_1608Metric_Pad0.98x0.95mm_HandSolder
R13, R14, R15, R16: 1K; R_0603_1608Metric_Pad0.98x0.95mm_HandSolder
R17: 72.5K; R_0603_1608Metric_Pad0.98x0.95mm_HandSolder
RV1: R_Potentiometer; Potentiometer_Piher_PT-10-V10_Vertical
TP3, TP4: TestPoint; PinHeader_1x01_P2.54mm_Vertical
U3: ADA4807-4ARUZ; TSSOP-14_4.4x5mm_P0.65mm
U8: MCP1501-18xCH; SOT-23-6

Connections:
+3.3V: C5.2, C19.1, C21.1, U3.4 (V+), U8.4 (~SHDN), U8.6 (VDD); also elsewhere on the board
-3V3: C20.1, C22.1, U3.11 (V-); also elsewhere on the board
/EMG_ADC/AdcCh0: J2.2, R5.1, U3.14; also elsewhere on the board
/EMG_ADC/AdcCh1: C18.1, J2.1, R17.1; also elsewhere on the board
/EMG_FrontEnd/LP_OUT: U3.3 (+); also elsewhere on the board
Earth: C5.1, C7.1, C18.2, C19.2, C20.2, C21.2, C22.2, R7.2, R13.2, R15.1, U8.2 (GND), U8.3 (GND), U8.5 (GND); also elsewhere on the board
unnamed: C17.2, D3.2 (A), R14.2, U3.2 (-)
unnamed: C17.1, D3.1 (K), D4.2 (A), U3.1
unnamed: D4.1 (K), R15.2, U3.5 (+)
unnamed: R17.2, RV1.1, TP4.1 (1_1), U3.8
unnamed: R14.1, R16.2, U3.6 (-)
unnamed: R16.1, TP3.1 (1_1), U3.7, U3.10 (+)
unnamed: R13.1, RV1.2, U3.9 (-)
unnamed: R4.1, R6.1, U3.12 (+)
unnamed: R5.2, R7.1, U3.13 (-)
unnamed: C7.2, R6.2, U8.1 (OUT)

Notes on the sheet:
Final low pass filter cutoff frequency is 1 Hz
Adding 1.8V so negative voltage is not applied to ADC
Precision full wave rectifier circuit. See: TI Precision Designs: Verified Design Precision Full-Wave Rectifier, Dual-Supply
Optional decoupling capacitors for the voltage reference. Provide extra filtering

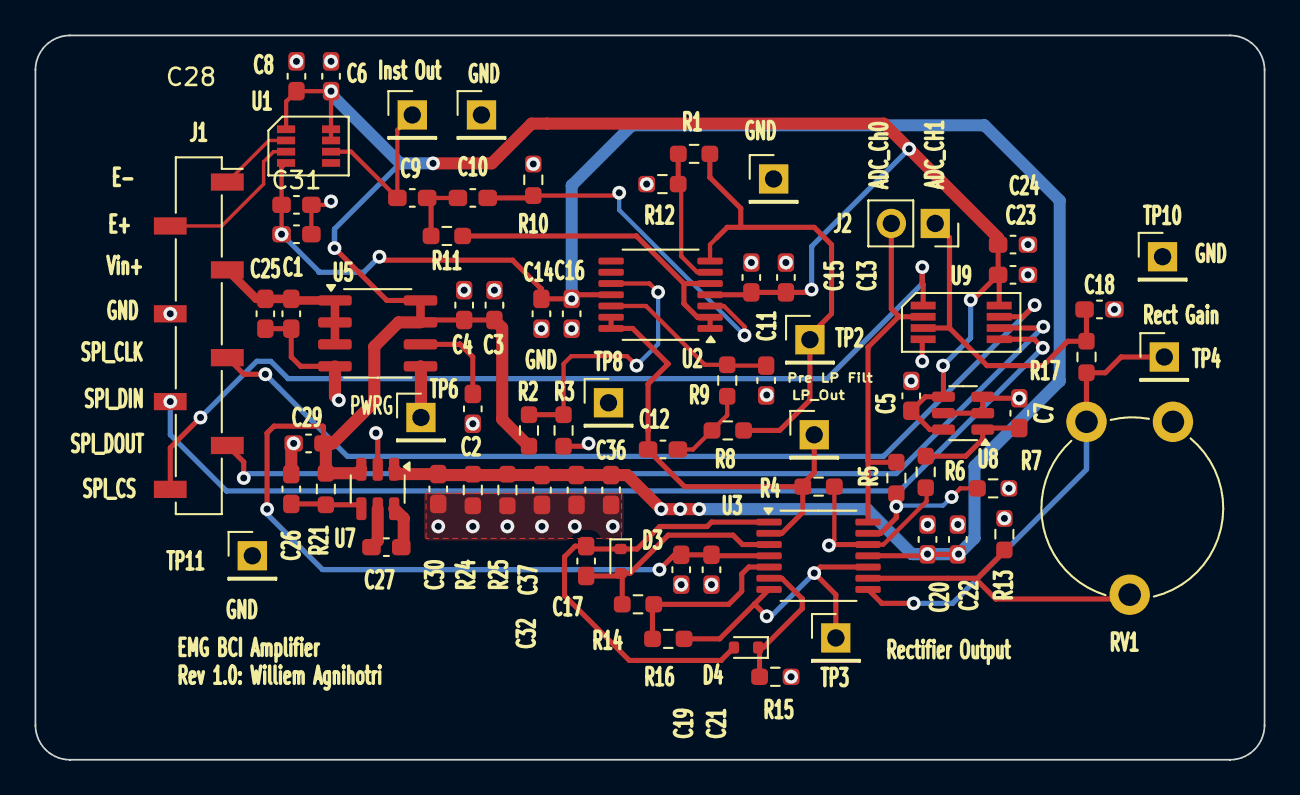
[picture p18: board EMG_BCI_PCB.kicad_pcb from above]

Board: 4 copper layers, 71.1 x 41.9 mm, 77 parts (0 on the bottom side), 37 nets.

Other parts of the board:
R2: 10k; R_0603_1608Metric_Pad0.98x0.95mm_HandSolder
R3: 2k; R_0603_1608Metric_Pad0.98x0.95mm_HandSolder

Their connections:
+3.3V: R2.1; also elsewhere on the board
Earth: R3.2; also elsewhere on the board
unnamed: R2.2, R3.1

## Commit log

2025-09-20 Add files from old front-end schematic
    [EMG_ADC.sch, EMG_BCI_PCB-job.gbrjob, EMG_BCI_PCB.kicad_pcb, EMG_BCI_PCB.sch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]
2025-09-20 Change to instrumnetation amplifier and filter circuitry
    [EMG_ADC.kicad_sch, EMG_BCI_PCB.kicad_sch, EMG_FrontEndsch.kicad_sch, EMG_Rect.kicad_sch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]
2025-09-21 More schematic changes
    [EMG_ADC.kicad_sch, EMG_BCI_PCB.kicad_sch, EMG_FrontEndsch.kicad_sch, EMG_Rect.kicad_sch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]
2025-09-21 Added power symbols for +/-3.3V
    [EMG_ADC.kicad_sch, EMG_BCI_PCB.kicad_sch, EMG_FrontEndsch.kicad_sch, EMG_Rect.kicad_sch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]
2025-09-21 Removed some warnings from the electrical rules
    [EMG_ADC.kicad_sch, EMG_BCI_PCB.kicad_sch, EMG_FrontEndsch.kicad_sch, EMG_Rect.kicad_sch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]
2025-09-21 Assigned footprints to components
    [EMG_ADC.kicad_sch, EMG_FrontEndsch.kicad_sch, EMG_Rect.kicad_sch, Power.kicad_sch]
2025-09-21 Removed inductors on power lines
    [Power.kicad_sch]
2025-12-07 finally assigned the footprints to the schematic symbols
    [EMG_ADC.kicad_sch, EMG_BCI_PCB.kicad_sch, EMG_FrontEndsch.kicad_sch, EMG_Rect.kicad_sch]
2025-12-07 Ran ERC again
    [EMG_FrontEndsch.kicad_sch, EMG_Rect.kicad_sch]
2025-12-07 Imported footprints into layout
    [EMG_BCI_PCB.kicad_pcb, EMG_Rect.kicad_sch]
2025-12-08 Initial placement and routing
    [EMG_ADC.kicad_sch, EMG_BCI_PCB.kicad_sch, EMG_FrontEndsch.kicad_sch, EMG_Rect.kicad_sch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]
2025-12-31 Ordering the components
    [EMG_BCI_PCB-B_Cu.gbr, EMG_BCI_PCB-B_Mask.gbr, EMG_BCI_PCB-B_Silkscreen.gbr, EMG_BCI_PCB-Edge_Cuts.gbr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]
2025-12-31 Removes unecessary files
    [EMG_BCI_PCB-B_Cu.gbr, EMG_BCI_PCB-B_Mask.gbr, EMG_BCI_PCB-B_Silkscreen.gbr, EMG_BCI_PCB-Edge_Cuts.gbr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]
2026-04-26 PCB completed, and assembled
    [EMG_BCI_PCB.csv]
2026-05-06 Adds finished simulation of circuits
2026-05-18 Document test results for instrumentation amplifier
    Added test results and analysis for the instrumentation amplifier and filtering stages, including tables of input/output data and observations on performance.
2026-05-18 Add the negative voltage supply to the instrumentation amplifier
    [EMG_ADC.kicad_sch, EMG_BCI_PCB.kicad_sch, EMG_FrontEndsch.kicad_sch, EMG_Rect.kicad_sch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]
2026-05-18 corrected the active rectifier schematic
    [EMG_Rect.kicad_sch]
2026-05-20 Adjusts PCB and schematic with changes
    [EMG_BCI_PCB.kicad_pcb]
